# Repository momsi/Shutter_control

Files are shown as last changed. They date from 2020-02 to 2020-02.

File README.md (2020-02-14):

# Shutter control

This repo contains all code used for the new shutter control unit for the Arc-PVD in the NETZ 2.48 lab.

## Operation
### Before use while processing
* Switch on the power supply
* confirm correct shutter movement
* calibrate the shutter if necessary 
  * adjust the open position by rotating the motor by hand
  * open and close the shutter
  * adjust position again

### Manual Mode
In manual mode the shutter opens by depressing the trigger switch. The time the shutter is open will be shown in seconds on the display. Close the shutter by depressing the trigger switch again. The diplay will reset to "manual".

### Auto mode
In auto mode, the shutter opens and closes automatically after a predetermined time.

To set the time, use the keypad:
* reset the timer by pressing \*
* enter the desired time in seconds
* confirm by pressing \#
* the set time will be shown in the display

To open the shutter, press the trigger switch. The shutter opens and the time open will be counted down in the display. The shutter closes automatically when the timer reaches 0.

### Emergency abort
The red emergency abort switch is only active when the shutter is opened. This button is intended to be used in case the program is unresponsive, __this is not a "_close the sutter_" switch__. 
The emergency abort switch s attached as a hardware interrupt and triggers the following routine:

1. Attempt to close the shutter
2. Disable motor power (so the motor can be closed manually in case of hardware failure)
3. Display ABORT
4. Delete and reset all variables
5. Reset the program

Again: __This is not a "_close the sutter_" switch__ and only to be used in case of 

## Hardware Conponents

Components    |  Used
------------- | -------------
Voltage regulator:   | L7806CV
Controller:          | Arduino Nano (ATmega328p)
Stepper controller:  | A4988
Stepper motor:       | QSH4218-35-10-027
Display              | SSD1306 (128x64)

Also some generic switches and a 4x4 Keypad

## Pinout / wiring
### Arduino
Pin    |  Connected to
------------- | -------------
D5-D12 | Keypad (left to right)
D4 | Mode Switch
D3 | Trigger
D2 | Emergency Abort
Upper GND | GND: Mode-Switch, Trigger, Emergency Abort 
A0 | Stepper Controller DIR 
A1 | Stepper Controller STEP
A2 | Stepper Controller ENABLE
A4 | Display SDA
A5 | Display SCL
5V | Display VCC, Stepper Controller VDD
Lower GND | Display GND, Stepper Controller GND
Vin | 6V supply from voltage regulator

### Voltage regulator

Pin    |  Connected to
------------- | -------------
1 (left) | 12V IN, Stepper Controller VMOT
2 (middle) | Arduino GND, Stepper Controller Motor GND
3 (right) | Arduino Vin

### Stepper Controller

Pin    |  Connected to
------------- | -------------
ENABLE | Arduino A2
RST | short to SLEEP
SLEEP | short to RST
STEP  | Arduino A1
DIR  | Arduino A0
VMOT | 12V IN
GND | Voltage regulator GND
2A, 2B | Motor Coil 2
1A, 1B | Motor Coil 1
VDD | Arduino 5V
GND | Arduino GND

### Display 

Pin    |  Connected to
------------- | -------------
VCC | Arduino 5V
GND | Arduino GND
SDA | Arduino A4
SCL | Arduino A5

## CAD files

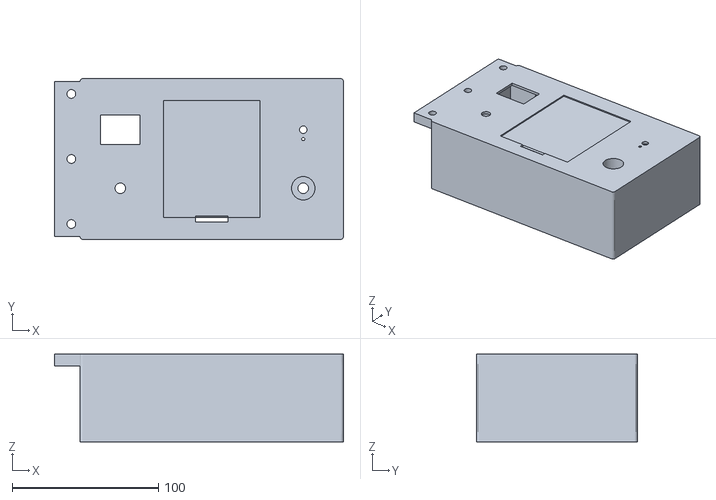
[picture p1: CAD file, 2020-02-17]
3D CAD Files/Shutterbox_front.stl
197.5 x 110.0 x 60.0

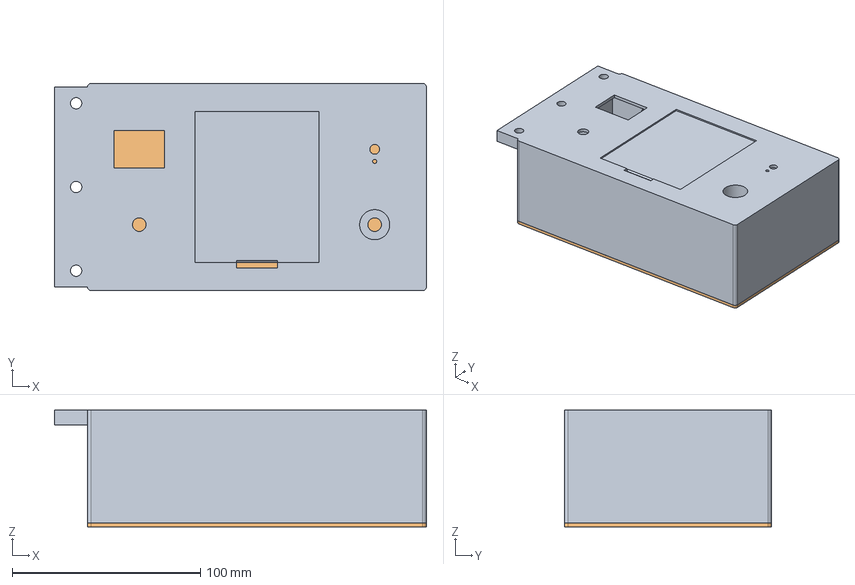
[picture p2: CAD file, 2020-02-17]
3D CAD Files/Shutterbox .step
197.5 x 110.0 x 62.0 mm
Shutterbox_1
Shutterbox Deckel
92010A128 x 2

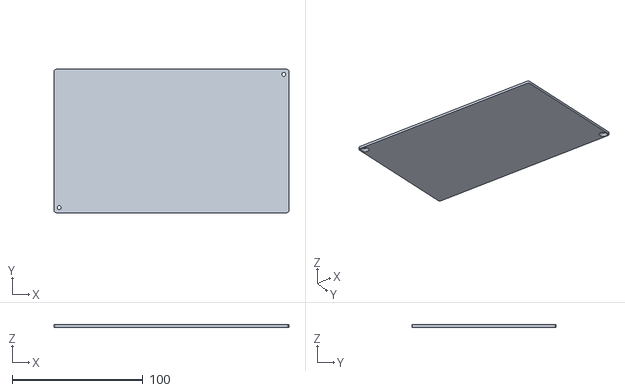
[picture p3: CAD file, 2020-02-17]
3D CAD Files/Shutterbox Deckel.stl
180.0 x 110.0 x 2.00

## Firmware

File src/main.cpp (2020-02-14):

/*--------------To do

*/


/*-------------Setup
Using an Arduino with AT Mega 328p

Keypad: generic 4x4 (non serial)
    Attach to Pins (from left to right): 12,11,10,9,8,7,6,5

Display: SSD1306 128 x 64 OLED
    Attach PINS:  VCC:5V
                  GND:GND
                  SCL:A5
                  SDA:A4
    I2C Adress:   0x3C

Stepper Driver: A4988
    Attach PINS:  VMOT: 12V PSU
                  MOTGND: GND of 12V PSU
                  1A, 2A, 1B, 2B: Phases of stepper
                  VDD: 5V
                  GND: GND
                  DIR: A0
                  STEP: A1
                  RST: short to SLEEP
                  SLEEP: short to RST
                  ENABLE: A2
Mode Switch:
    Attach to PIN D4
    Pullup!:  LOW is Auto-mode
              HIGH is Manual-mode

Shutter-Trigger:
    Attach to PIN D3 and GND
    Pullup!:  Is triggered when pulled to GND

Abort-Trigger:
    Attach to PIN D2 and GND
    Pullup!:  Is triggered when pulled to GND
    INTERRUPT: Needs to be attached to an interrupt PIN, confirm if using different controller
*/

#include <Arduino.h>
#include <keypad.h>
#include <Wire.h>
#include <Adafruit_SSD1306.h>

//---------------- Variables
int INTERNAL_LED_PIN = 13;
int MODE_SWITCH_PIN = 4;
int TRIGGER_BUTTON_PIN = 3;
int EMERGENCY_ABORT_PIN =2;

const int enablePin = A2; // Stepper Controller ENABLE pin is attached to this pin
const int stepPin = A1; // Stepper Controller STEP pin is attached to this pin
const int dirPin = A0; // Stepper Controller DIR pin is attached to this pin
const int steps_per_rev = 200; // sets the steps per revolution, might need tuning over time
const int step_delay = 4; // delay between STEP HIGH and LOW. Controlls rotation speed. Might need tuning depending on torque and overswing

volatile bool EMERGENCY_ABORT_CALLED=false;
volatile bool AUTO_MODE_ENABLED;
volatile int time_to_open=0;
volatile unsigned long time_sutter_was_opened=0;
volatile unsigned long time_open=0;

//---------------- Keypad
const byte numRows=4;
const byte numCols=4;
char keymap[numRows][numCols] ={
  {'1','2','3','A'},
  {'4','5','6','B'},
  {'7','8','9','C'},
  {'*','0','#','D'}};
byte rowPins[numRows] = {12,11,10,9};
byte colPins[numCols] = {8,7,6,5};
Keypad keypad = Keypad(makeKeymap(keymap),rowPins,colPins,numRows,numCols);

//---------------- Display
#define OLED_RESET 4
Adafruit_SSD1306 display(OLED_RESET);

//----------------------------------

void emergency_abort(){
  delay(200);
  EMERGENCY_ABORT_CALLED=true;
}

void shutter_open(){
  digitalWrite(INTERNAL_LED_PIN,HIGH);
  digitalWrite(enablePin,LOW);
  digitalWrite(dirPin,LOW);
  delay(100);
  for (int i = 0; i < steps_per_rev; i++) {
    digitalWrite(stepPin, HIGH);
    delay(step_delay);
    digitalWrite(stepPin, LOW);
    delay(step_delay);}
  digitalWrite(enablePin,HIGH);
}

void shutter_close(){
  digitalWrite(INTERNAL_LED_PIN,LOW);
  digitalWrite(enablePin,LOW);
  digitalWrite(dirPin,HIGH);
  delay(100); 
  for (int i = 0; i < steps_per_rev; i++) {
    digitalWrite(stepPin, HIGH);
    delay(step_delay);
    digitalWrite(stepPin, LOW);
    delay(step_delay);}
  digitalWrite(enablePin,HIGH);
}

void abort(){
  shutter_close();
  EMERGENCY_ABORT_CALLED=false;
  time_open=0;
  time_to_open=0;
  time_sutter_was_opened=0;
  display.clearDisplay();
  display.setTextSize(2);
  display.setTextColor(WHITE);
  display.setCursor(20, 10);
  display.println("ABORTED");
  display.display();
  delay(2000);
  asm volatile ("  jmp 0");
  EMERGENCY_ABORT_CALLED=false;
}

void display_menu_auto(int time){
  display.clearDisplay();
  display.setTextSize(2);
  display.setTextColor(WHITE);
  display.setCursor(0, 10);
  display.print("time: ");
  display.print(time);
  display.display();
}

void display_menu_manual(){
  display.clearDisplay();
  display.setTextSize(2);
  display.setTextColor(WHITE);
  display.setCursor(30, 10);
  display.print("Manual");
  display.display();
}

void display_refresh(int time){
  display.clearDisplay();
  display.setTextSize(3);
  display.setTextColor(WHITE);
  display.setCursor(50, 5);
  display.println(time);
  display.display();
}

void shutter_auto(){
  int time_remaining=time_to_open;
  unsigned long millis_prev=0;
  attachInterrupt(digitalPinToInterrupt(EMERGENCY_ABORT_PIN), emergency_abort, FALLING);
  EMERGENCY_ABORT_CALLED=false;
  shutter_open();
  //if (EMERGENCY_ABORT_CALLED){abort();return;}
  while (time_remaining>=0){
    if (EMERGENCY_ABORT_CALLED){abort();return;}
    if (millis() - millis_prev >= 1000){
      millis_prev = millis();
      display_refresh(time_remaining);
      time_remaining--;}}
  shutter_close();
  detachInterrupt(digitalPinToInterrupt(EMERGENCY_ABORT_PIN));
  display_menu_auto(time_to_open);
}


int mode_auto(){
  static char userinput[4];
  static int count = 0;
  char key= keypad.getKey();
  static int input=0;

  if (AUTO_MODE_ENABLED==false){
    time_to_open=0;
    input=0;
    display.clearDisplay();
    display.setTextSize(2);
    display.setTextColor(WHITE);
    display.setCursor(40, 10);
    display.print("Auto");
    display.display();
    AUTO_MODE_ENABLED=true;}

  switch (key){
    case NO_KEY:
      break;

    case '#':   // Enter
      userinput[count] = '\0';
      input = atoi(userinput);
      time_to_open = input;
      display_menu_auto(time_to_open);
      break;

    case '*':   // Delete Input
      count = 0;
      memset(userinput,0,sizeof(userinput));
      input = 0;
      time_to_open = input;
      display_menu_auto(time_to_open);
      break;

    default:
      if (count < 3){     // Number entered
        userinput[count] = key;
        count+=1;
        break;}
      if (count==4){   // more than 3 chars input
        break;}}
return input;
}

void mode_manual(){
  if (AUTO_MODE_ENABLED==true){
    display.clearDisplay();
    display.setTextSize(2);
    display.setTextColor(WHITE);
    display.setCursor(30, 10);
    display.print("Manual");
    display.display();
    AUTO_MODE_ENABLED=false;}
}

void trigger_depressed(){
  if (AUTO_MODE_ENABLED==true && time_to_open!=0){
    shutter_auto();}
  else if (AUTO_MODE_ENABLED==true && time_to_open==0){
    display.clearDisplay();
    display.setTextSize(2);
    display.setTextColor(WHITE);
    display.setCursor(0, 10);
    display.print("set time!!");
    display.display();
    delay(1000);
    display_menu_auto(0);}
  else if (AUTO_MODE_ENABLED==false){
    int time_next_refresh=0;
    bool close_shutter=0;
    attachInterrupt(digitalPinToInterrupt(EMERGENCY_ABORT_PIN), emergency_abort, FALLING);
    EMERGENCY_ABORT_CALLED=false;
    shutter_open();
    time_sutter_was_opened=millis();
    while (!close_shutter){
      if (EMERGENCY_ABORT_CALLED){
        abort();return;}
      time_open=millis()-time_sutter_was_opened;
      time_open=time_open/1000;
      if(time_open-time_next_refresh>=1){
        display_refresh(time_open);
        time_next_refresh++;}
      if (digitalRead(TRIGGER_BUTTON_PIN)==0){
        shutter_close();
        detachInterrupt(digitalPinToInterrupt(EMERGENCY_ABORT_PIN));
        close_shutter=true;
        delay(200); // for debouncing --- could be replaced with millis(), but not urgently needed due to small duration
        display_menu_manual();}}}
}

//----------------------------------

void setup() {
  delay(100);
  EMERGENCY_ABORT_CALLED=false;
  delay(100);
  pinMode(enablePin, OUTPUT);
  digitalWrite(enablePin,HIGH);
  pinMode(stepPin, OUTPUT);
  digitalWrite(stepPin,LOW);
  pinMode(dirPin, OUTPUT);
  digitalWrite(dirPin,LOW);
  pinMode(INTERNAL_LED_PIN,OUTPUT);
  pinMode(MODE_SWITCH_PIN,INPUT_PULLUP);
  pinMode(TRIGGER_BUTTON_PIN,INPUT_PULLUP);
  pinMode(EMERGENCY_ABORT_PIN,INPUT_PULLUP);
  //attachInterrupt(digitalPinToInterrupt(EMERGENCY_ABORT_PIN), emergency_abort, FALLING);
  //detachInterrupt(digitalPinToInterrupt(EMERGENCY_ABORT_PIN));
  delay(500);
  time_open = 0;
  time_to_open = 0;
  time_sutter_was_opened = 0;

  display.begin(SSD1306_SWITCHCAPVCC, 0x3C);

  if (digitalRead(MODE_SWITCH_PIN)==0){
    AUTO_MODE_ENABLED=true;
    display.clearDisplay();
    display.setTextSize(2);
    display.setTextColor(WHITE);
    display.setCursor(40, 10);
    display.print("Auto");
    display.display();}
  else{
    AUTO_MODE_ENABLED=false;
    display.clearDisplay();
    display.setTextSize(2);
    display.setTextColor(WHITE);
    display.setCursor(30, 10);
    display.print("Manual");
    display.display();}

  EMERGENCY_ABORT_CALLED=false;
  digitalWrite(enablePin,HIGH);
}

void loop() {
  digitalRead(MODE_SWITCH_PIN)==0 ? mode_auto():0;
  digitalRead(MODE_SWITCH_PIN)==1 ? mode_manual():void();
  if (digitalRead(TRIGGER_BUTTON_PIN)==0){
    delay(200); // for debouncing --- could be replaced with millis(), but not urgently needed due to small duration
    trigger_depressed();}
  //if (EMERGENCY_ABORT_CALLED){
  //  abort();}
}

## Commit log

2020-01-16 introduced motor logic - debounced abort
2020-02-17 Added CAD Data for the Box
    Contains Step Model of the Box and .STL files for 3d printing
    [Shutterbox .step, Shutterbox Deckel.stl, Shutterbox_front.stl]
